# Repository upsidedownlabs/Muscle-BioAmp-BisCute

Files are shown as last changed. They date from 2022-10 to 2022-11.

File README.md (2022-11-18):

# Muscle BioAmp BisCute

 



 
 


Muscle BioAmp BisCute is a cute DIY EMG sensor for precise ElectroMyoGraphy (EMG) at an affordable cost. It comes with a fixed gain of x2420 and BandPass filter of 72Hz - 720Hz. To record the EMG signals you can use any standalone ADC like ADS1115 or any microcontroller development board with an ADC of your choice like Arduino UNO/Nano.

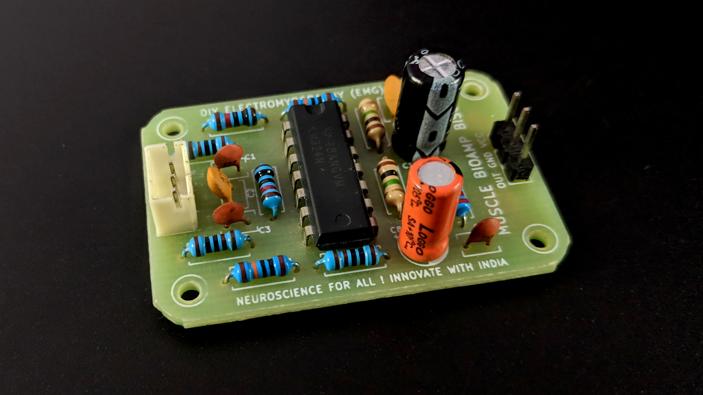
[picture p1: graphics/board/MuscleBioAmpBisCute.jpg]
Upside Down Labs BioAmp EXG Pill Assembled


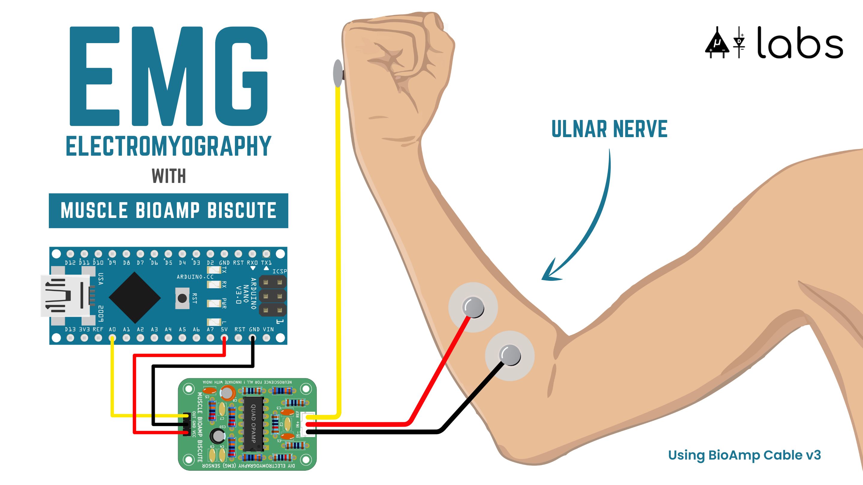
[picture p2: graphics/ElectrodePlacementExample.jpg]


## Hardware

Muscle BioAmp Biscute has been created using KiCad and all the design files can be found under [hardware](hardware/) folder. Images below shows a quick overview of the hardware design.

| PCB Front           |  PCB Back |
| :-------------------------: | :-------------------------: |
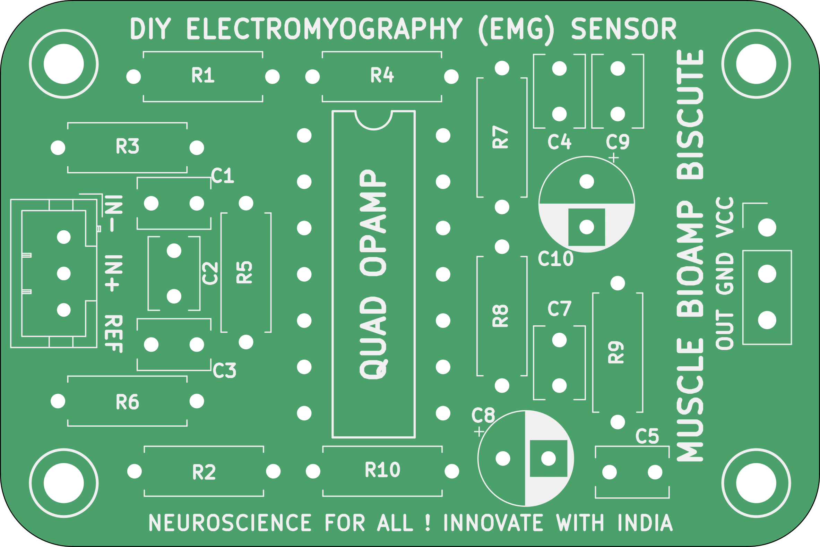
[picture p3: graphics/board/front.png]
Upside Down Labs Muscle BioAmp BisCute front
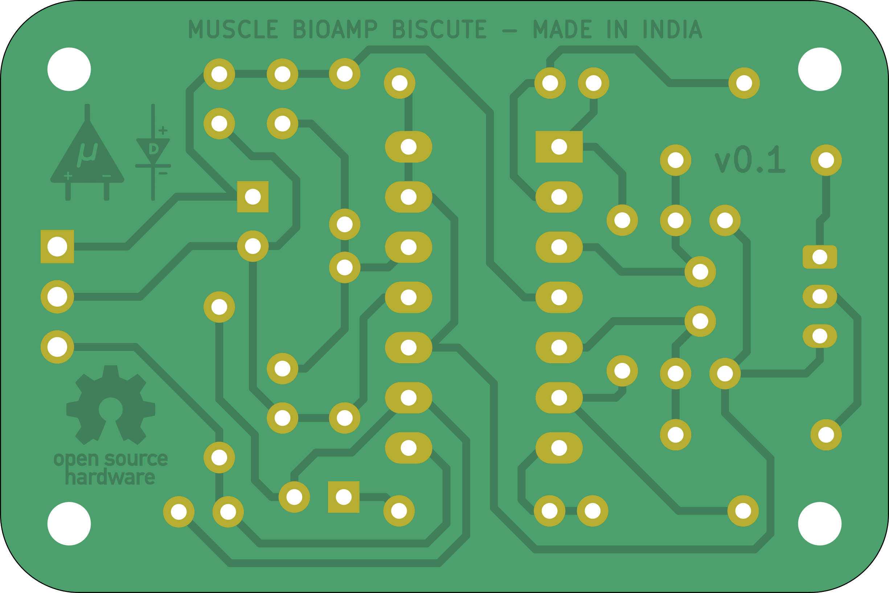
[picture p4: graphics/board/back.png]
Upside Down Labs Muscle BioAmp BisCute back
|   |  |

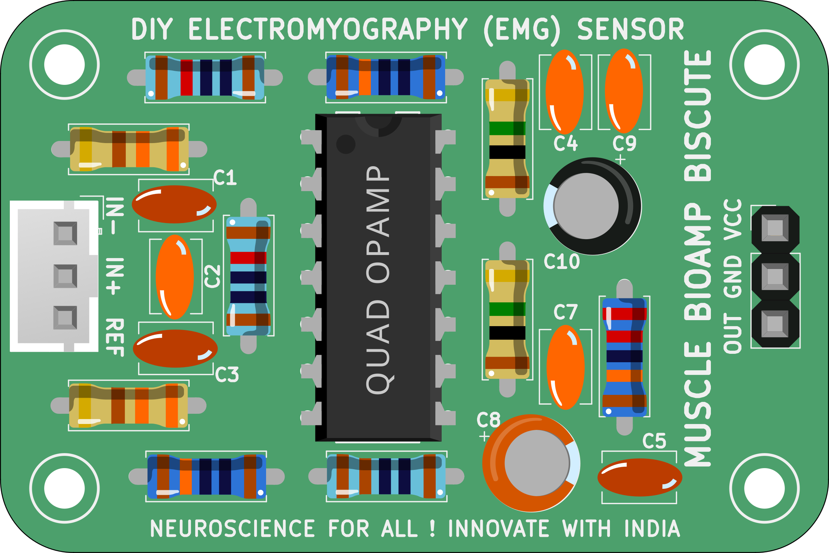
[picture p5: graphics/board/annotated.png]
Upside Down Labs Muscle BioAmp BisCute front annotated


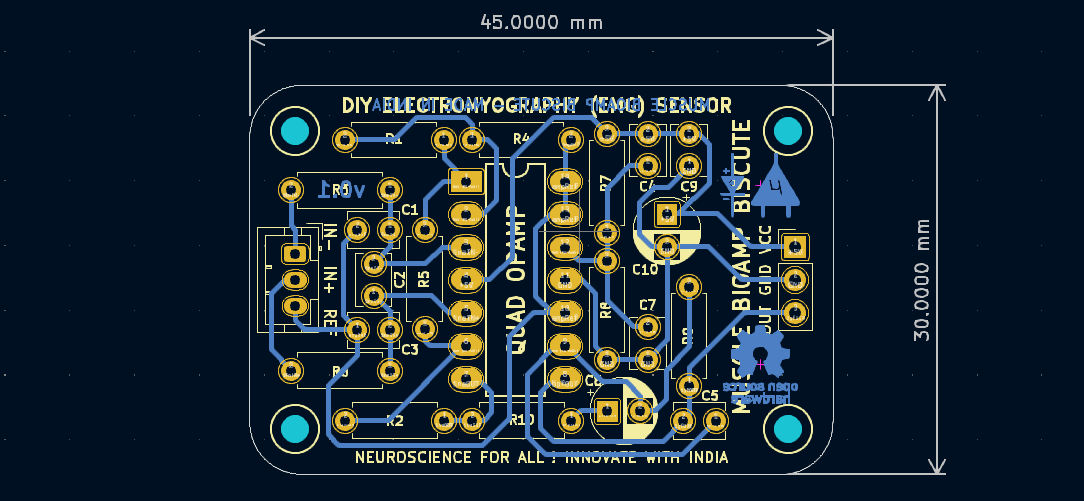
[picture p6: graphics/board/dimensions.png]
Upside Down Labs Muscle BioAmp BisCute dimensions


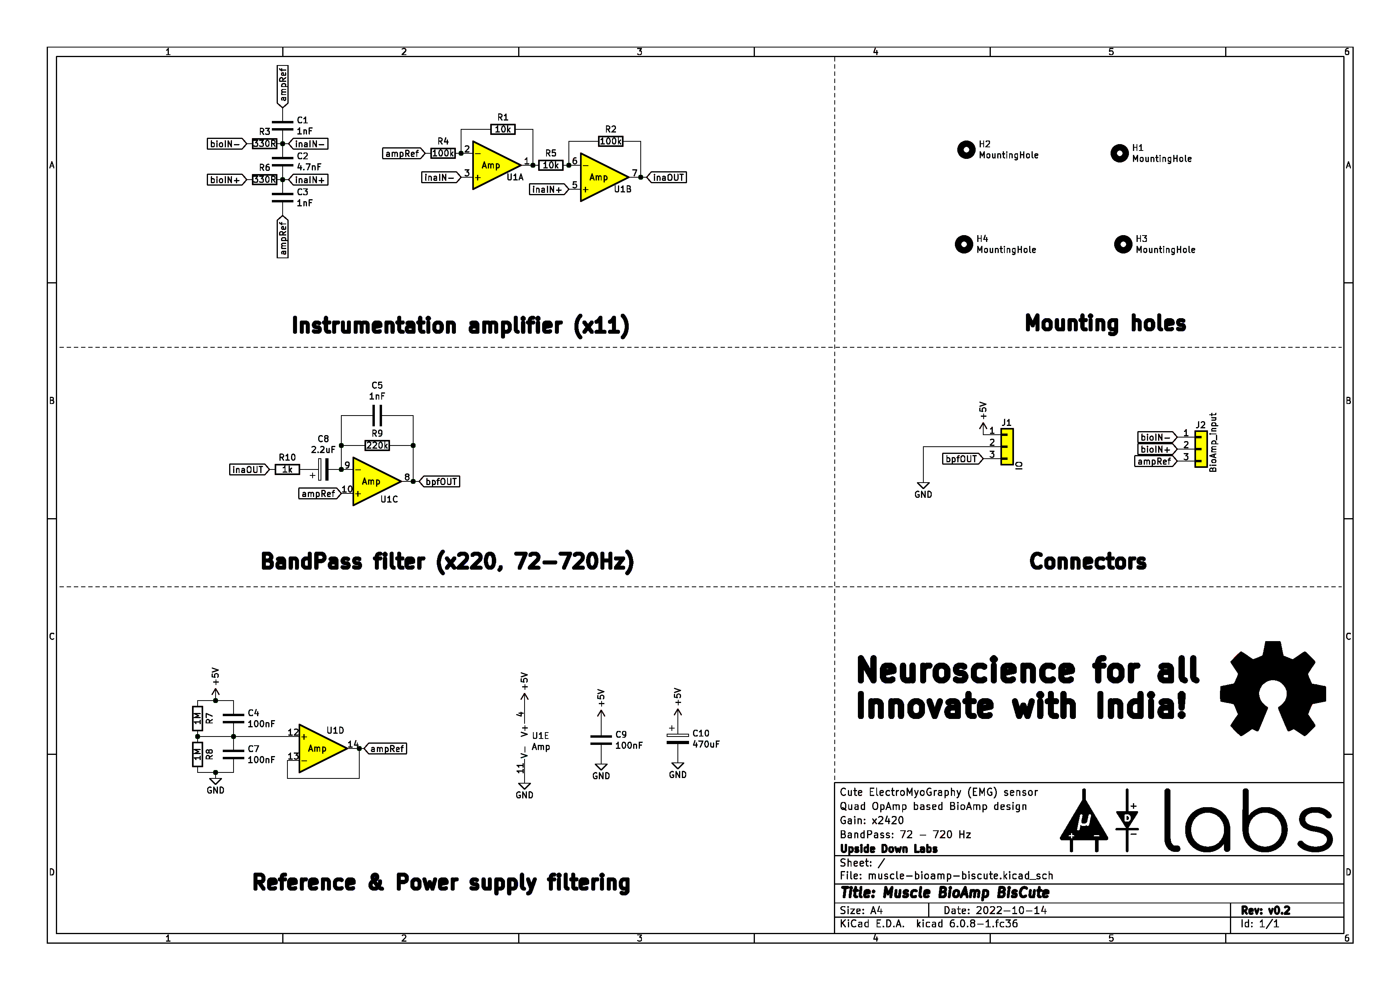
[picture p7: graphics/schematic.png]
Upside Down Labs Muscle BioAmp BisCute schematic


### Assembly

You can get your own Muscle BioAmp BisCute bag of parts from [our store](https://store.upsidedownlabs.tech/product/muscle-bioamp-biscute-diy/) or [Tindie](https://www.tindie.com/products/upsidedownlabs/muscle-bioamp-biscute-diy-muscle-sensor/) and for assembling your Biscute you can take a look at [this interactive BOM](https://upsidedownlabs.github.io/Muscle-BioAmp-BisCute/) or the step by step guide below. 

| Step 1 - Bare board | Step 2 - 100K Resistor | Step 3 - 10K Resistor| Step 4 - 1M Resistor|
| :----: | :----: | :----: | :----: |
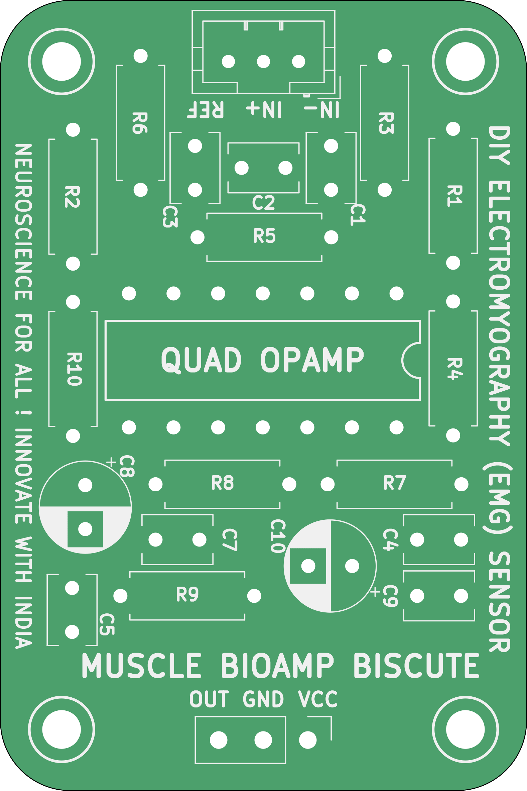
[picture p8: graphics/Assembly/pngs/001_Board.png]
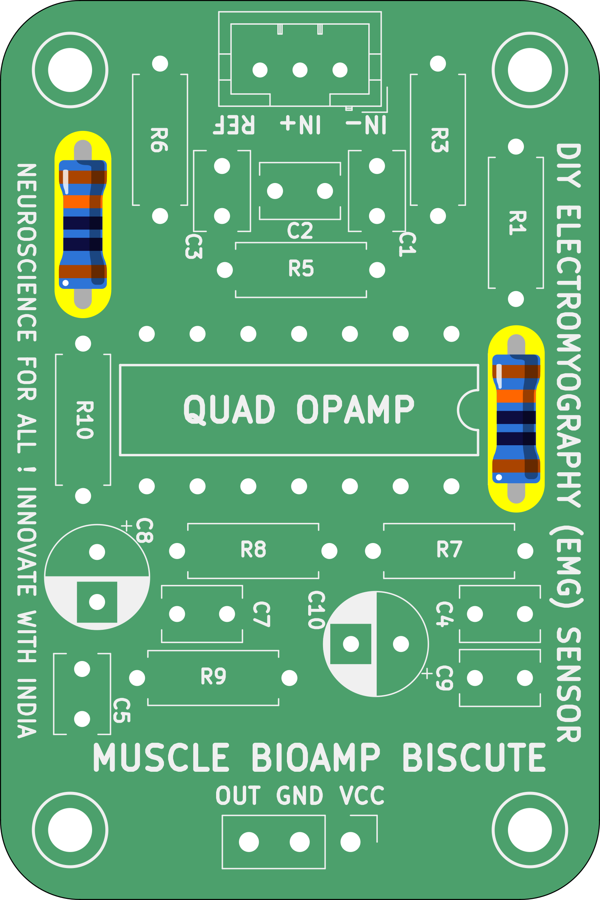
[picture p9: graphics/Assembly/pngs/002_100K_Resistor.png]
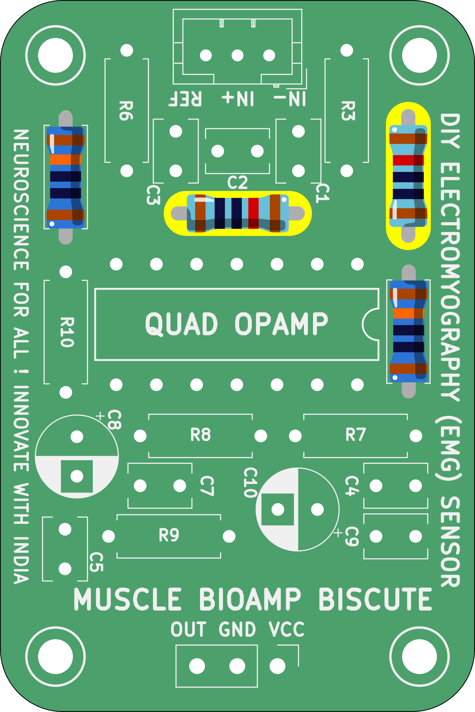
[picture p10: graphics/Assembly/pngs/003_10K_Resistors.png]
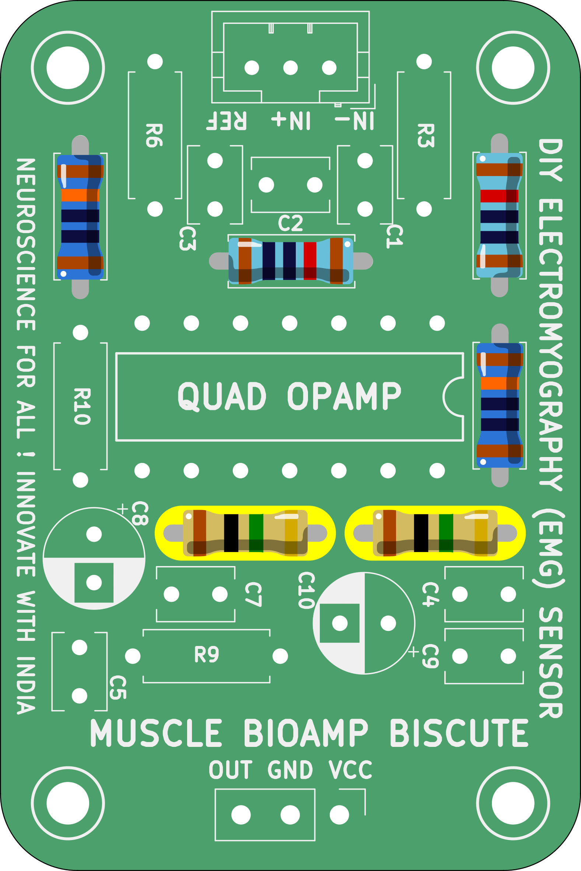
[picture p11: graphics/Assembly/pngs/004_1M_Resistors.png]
| ||||

| Step 5 - 330R Resistor | Step 6 - 220K Resistor | Step 7 - 4.7nF Capacitor | Step 8 - 2.2uF Capacitor |
| :----: | :----: | :----: | :----: |
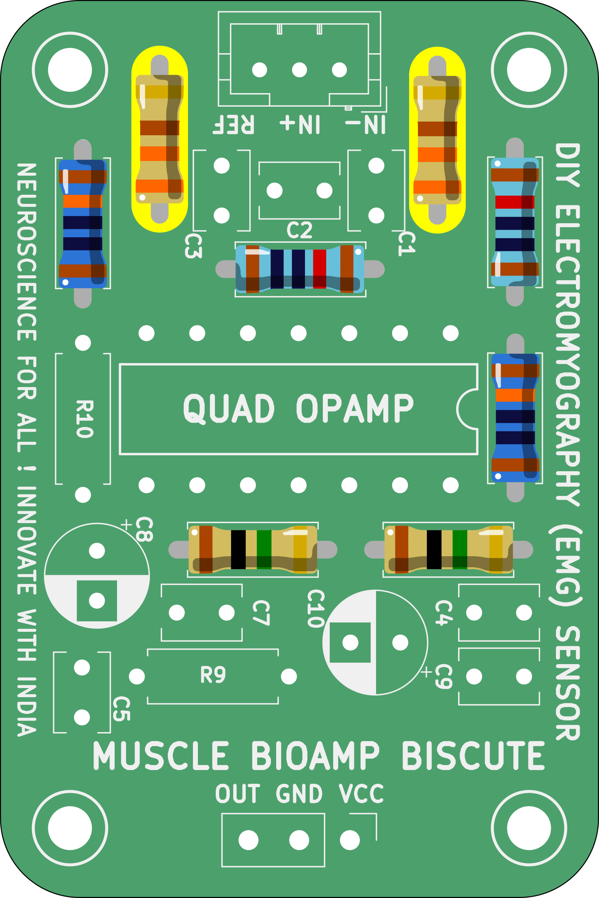
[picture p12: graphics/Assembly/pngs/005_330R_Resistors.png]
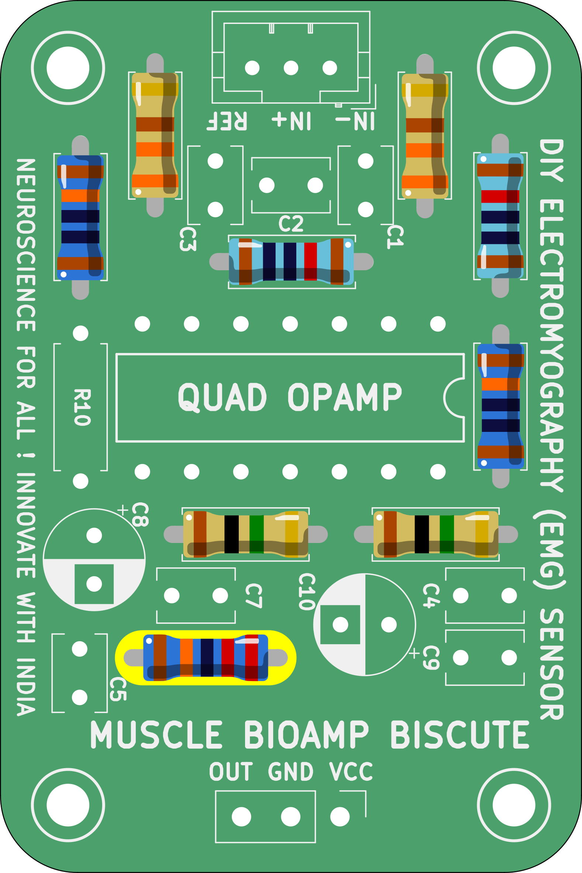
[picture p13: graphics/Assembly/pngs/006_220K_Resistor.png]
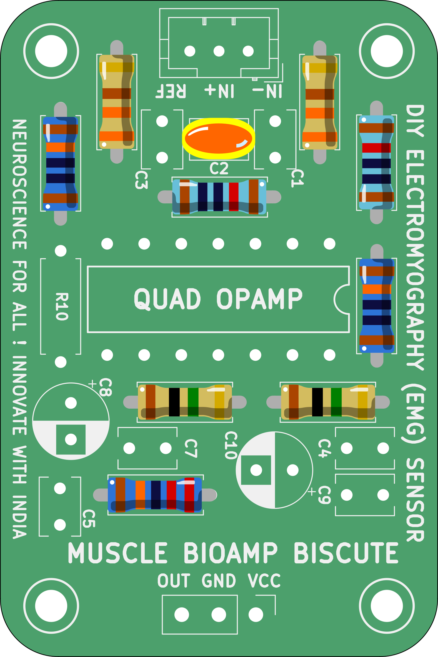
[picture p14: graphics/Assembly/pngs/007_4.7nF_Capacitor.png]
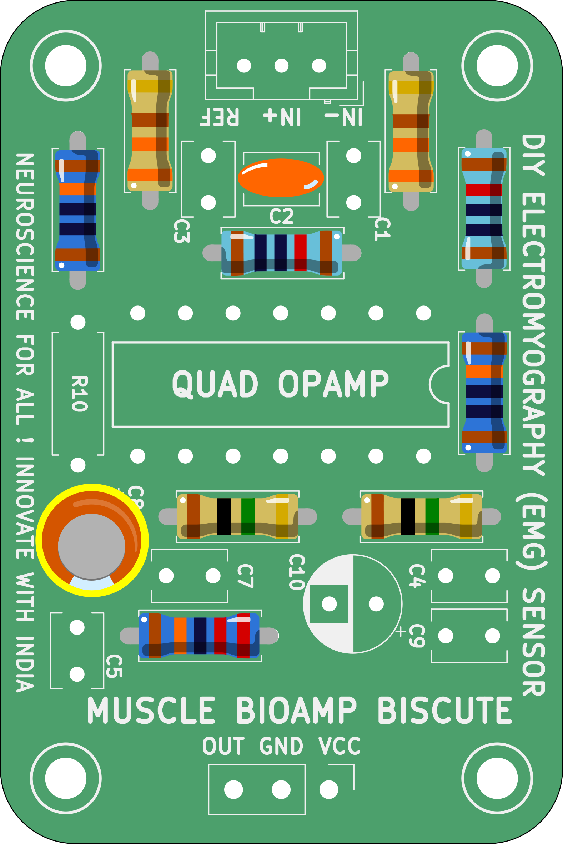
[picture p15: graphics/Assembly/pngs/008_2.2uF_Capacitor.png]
| ||||

| Step 9 - 470uF Capacitor | Step 10 - 100nF Capacitor | Step 11 - 1nF Capacitor | Step 13 - 1K Resistor |
| :----: | :----: | :----: | :----: |
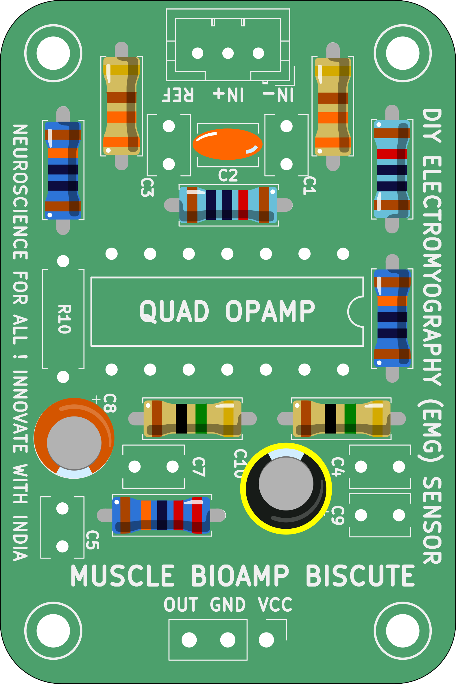
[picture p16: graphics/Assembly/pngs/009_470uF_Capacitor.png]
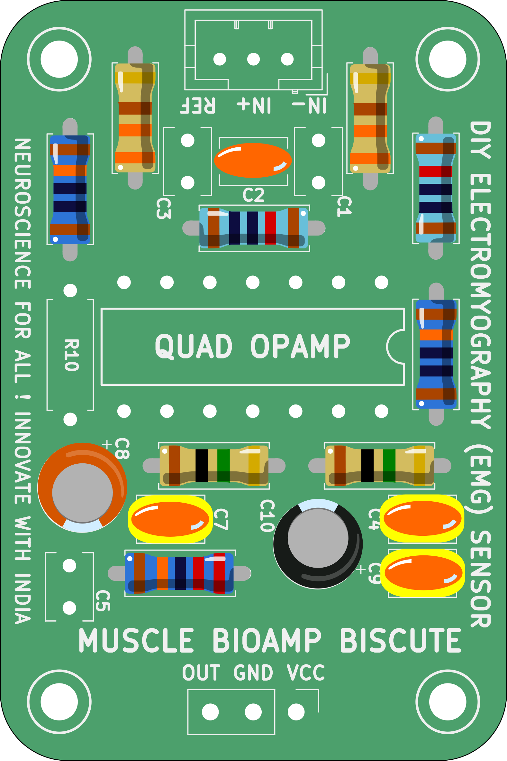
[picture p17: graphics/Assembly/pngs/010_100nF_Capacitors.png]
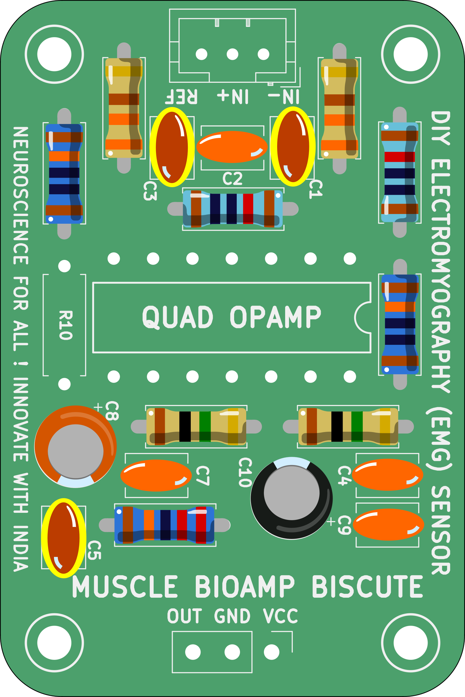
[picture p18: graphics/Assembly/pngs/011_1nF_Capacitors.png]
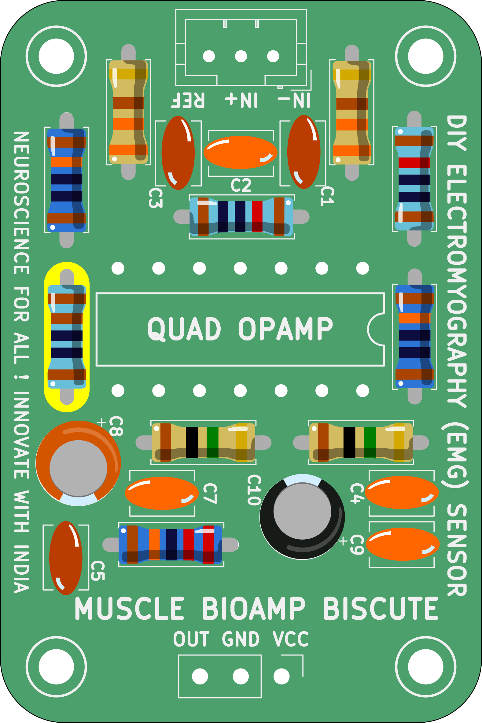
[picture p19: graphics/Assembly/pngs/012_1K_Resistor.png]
| ||||

| Step 13 - BioAmp Connector | Step 14 - Header Pin | Step 15 - IC | Step 16 - Biscute ready |
| :----: | :----: | :----: | :----: |
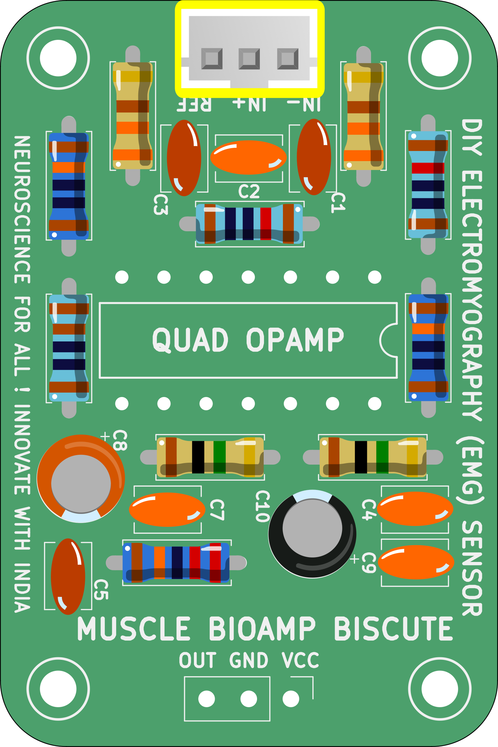
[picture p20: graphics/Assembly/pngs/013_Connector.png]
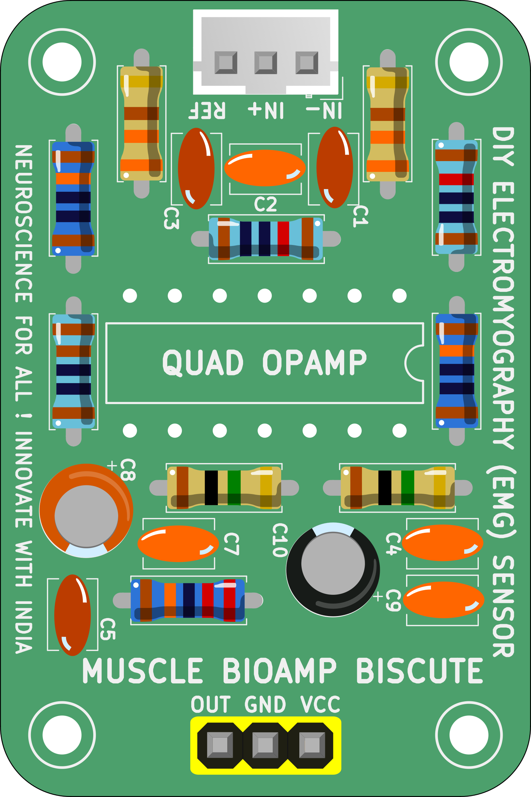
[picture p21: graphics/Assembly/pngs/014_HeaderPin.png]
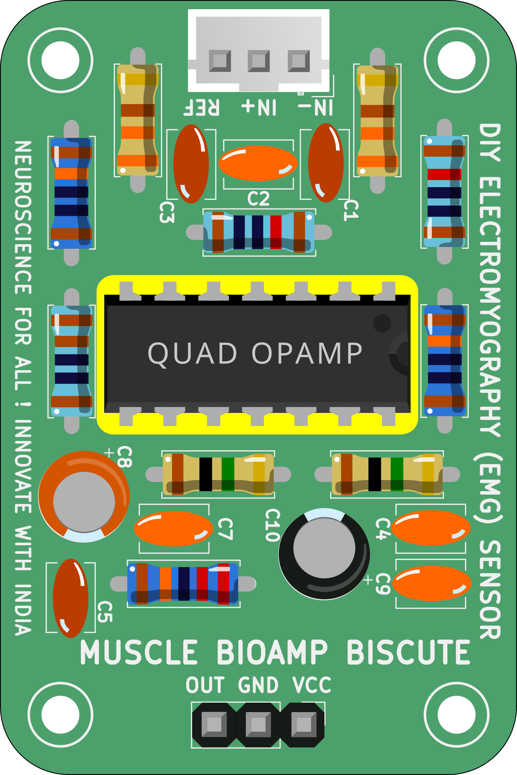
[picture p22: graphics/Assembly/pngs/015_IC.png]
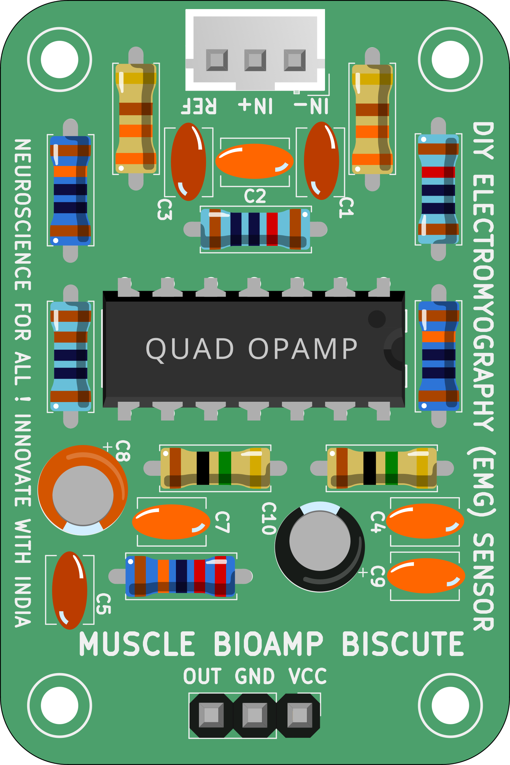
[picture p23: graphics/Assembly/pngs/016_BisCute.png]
| ||||

## License

| Licenses Facts              |  OSHWA Certification |
| :-------------------------: | :-------------------------: |
| <a href="LICENSE.md">Open Source Licenses Facts</a>  | <a href="https://certification.oshwa.org/in000039.html">Open Source Hardware Certification mark</a> | 

#### Hardware
CERN Open Hardware License Version 2 - Strongly Reciprocal ([CERN-OHL-S-2.0](https://spdx.org/licenses/CERN-OHL-S-2.0.html)).

#### Software
MIT open source [license](http://opensource.org/licenses/MIT).

#### Documentation:
<br />This work is licensed under a <a rel="license" href="http://creativecommons.org/licenses/by/4.0/">Creative Commons Attribution 4.0 International License</a>.

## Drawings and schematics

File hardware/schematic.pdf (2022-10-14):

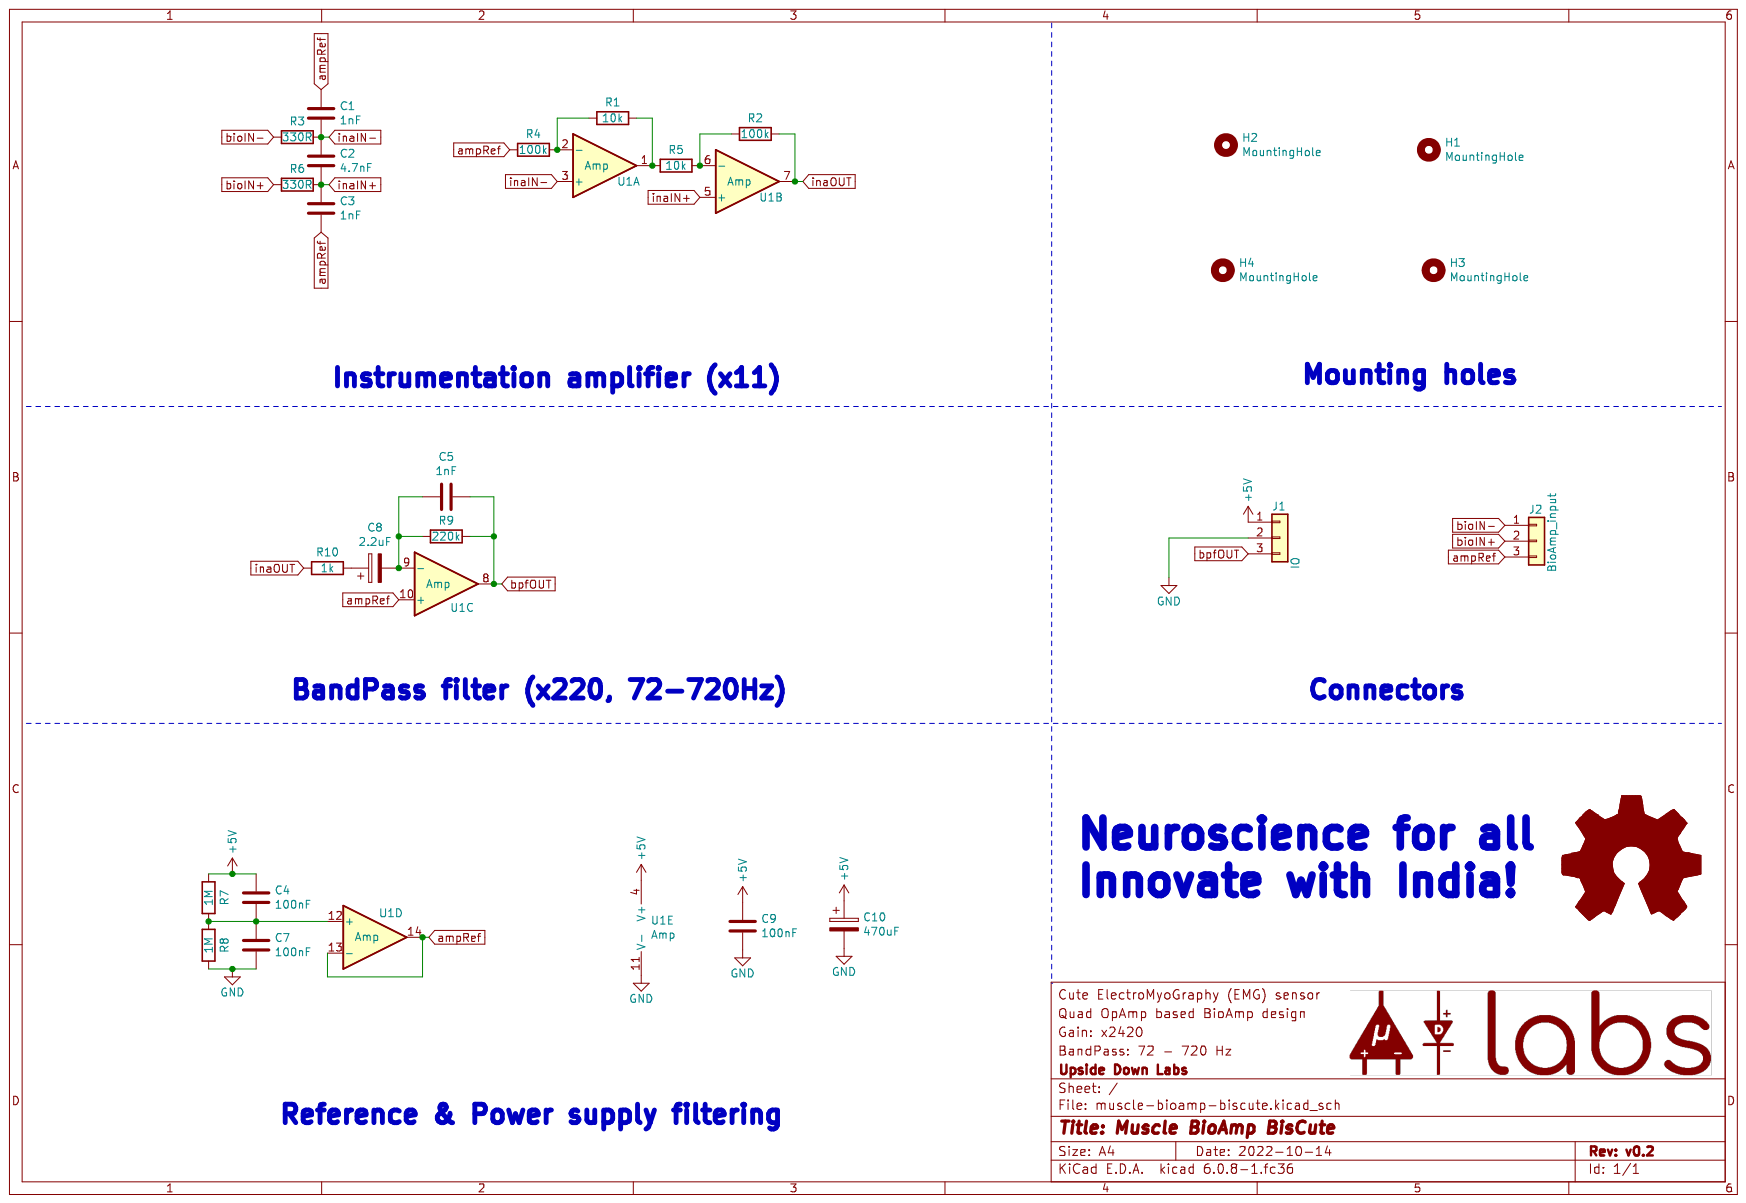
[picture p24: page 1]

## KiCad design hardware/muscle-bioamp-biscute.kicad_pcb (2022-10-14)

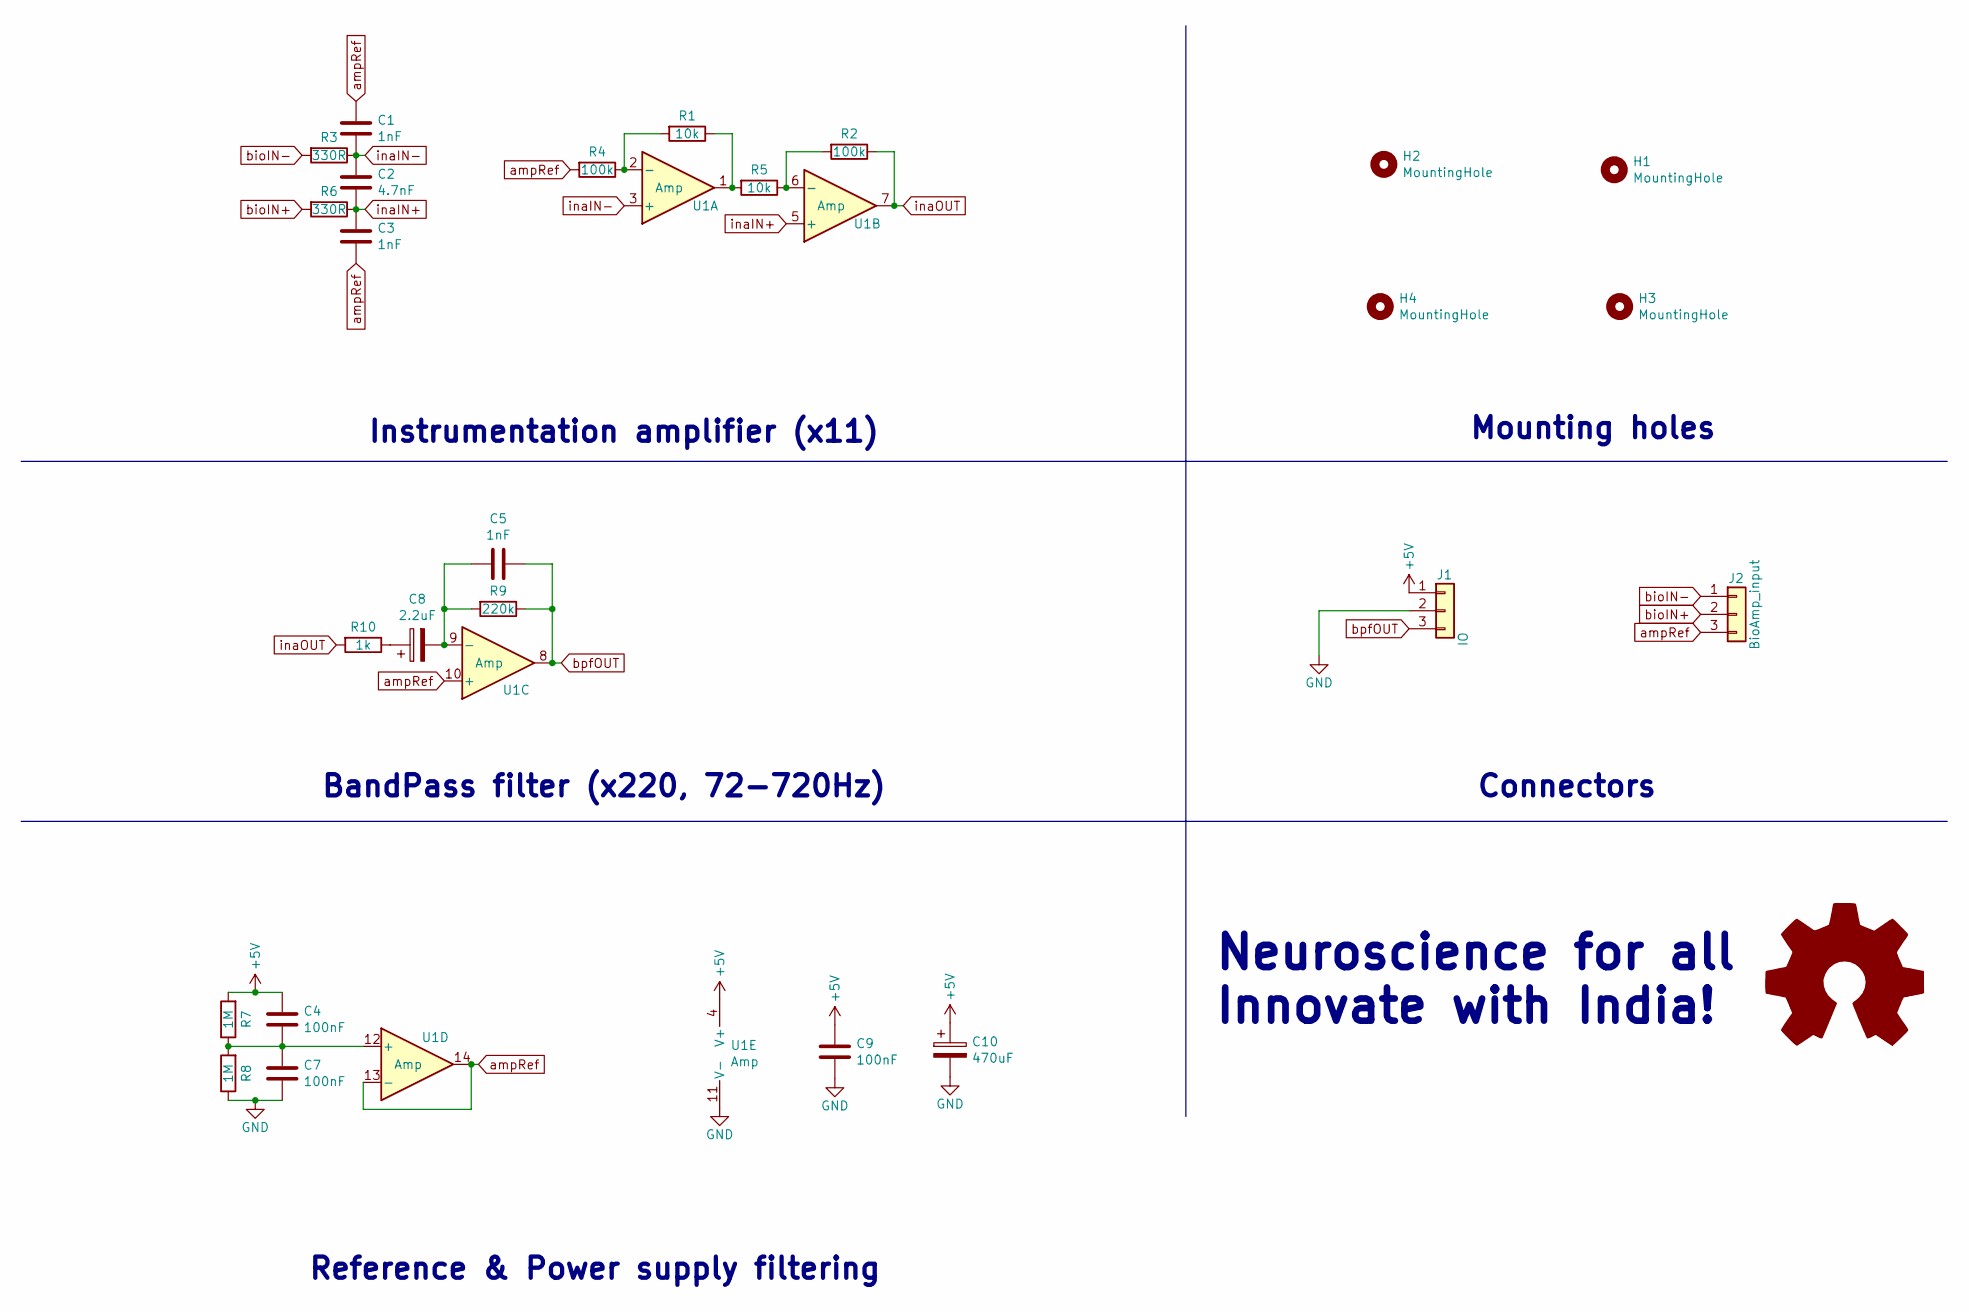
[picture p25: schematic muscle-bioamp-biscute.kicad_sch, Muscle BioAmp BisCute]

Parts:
C1, C3, C5: 1nF; C_Disc_D3.8mm_W2.6mm_P2.50mm
C2: 4.7nF; C_Disc_D3.8mm_W2.6mm_P2.50mm
C4, C7, C9: 100nF; C_Disc_D3.8mm_W2.6mm_P2.50mm
C8: 2.2uF; CP_Radial_D5.0mm_P2.50mm
C10: 470uF; CP_Radial_D5.0mm_P2.50mm
H1, H2, H3, H4: MountingHole; MountingHole_2.2mm_M2
J1: IO; PinHeader_1x03_P2.54mm_Vertical
J2: BioAmp_input; JST_PH_B3B-PH-K_1x03_P2.00mm_Vertical
R1, R5: 10k; R_Axial_DIN0207_L6.3mm_D2.5mm_P7.62mm_Horizontal
R2, R4: 100k; R_Axial_DIN0207_L6.3mm_D2.5mm_P7.62mm_Horizontal
R3, R6: 330R; R_Axial_DIN0207_L6.3mm_D2.5mm_P7.62mm_Horizontal
R7, R8: 1M; R_Axial_DIN0207_L6.3mm_D2.5mm_P7.62mm_Horizontal
R9: 220k; R_Axial_DIN0207_L6.3mm_D2.5mm_P7.62mm_Horizontal
R10: 1k; R_Axial_DIN0207_L6.3mm_D2.5mm_P7.62mm_Horizontal
U1: Amp; DIP-14_W7.62mm_LongPads

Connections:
+5V: C4.2, C9.2, C10.1, J1.1, R7.2, U1.4 (V+)
GND: C7.1, C9.1, C10.2, J1.2, R8.1, U1.11 (V-)
unnamed: C4.1, C7.2, R7.1, R8.2, U1.12 (+)
unnamed: C5.1, C8.2, R9.2, U1.9 (-)
unnamed: C8.1, R10.1
unnamed: R1.1, R5.2, U1.1
unnamed: R1.2, R4.1, U1.2 (-)
unnamed: R2.2, R5.1, U1.6 (-)
ampRef: C1.2, C3.1, J2.3, R4.2, U1.10 (+), U1.13 (-), U1.14
bioIN+: J2.2, R6.2
bioIN-: J2.1, R3.2
bpfOUT: C5.2, J1.3, R9.1, U1.8
inaIN+: C2.1, C3.2, R6.1, U1.5 (+)
inaIN-: C1.1, C2.2, R3.1, U1.3 (+)
inaOUT: R2.1, R10.2, U1.7

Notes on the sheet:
Instrumentation amplifier (x11)
Reference & Power supply filtering
Neuroscience for all Innovate with India!
Connectors
BandPass filter (x220, 72-720Hz)
Mounting holes

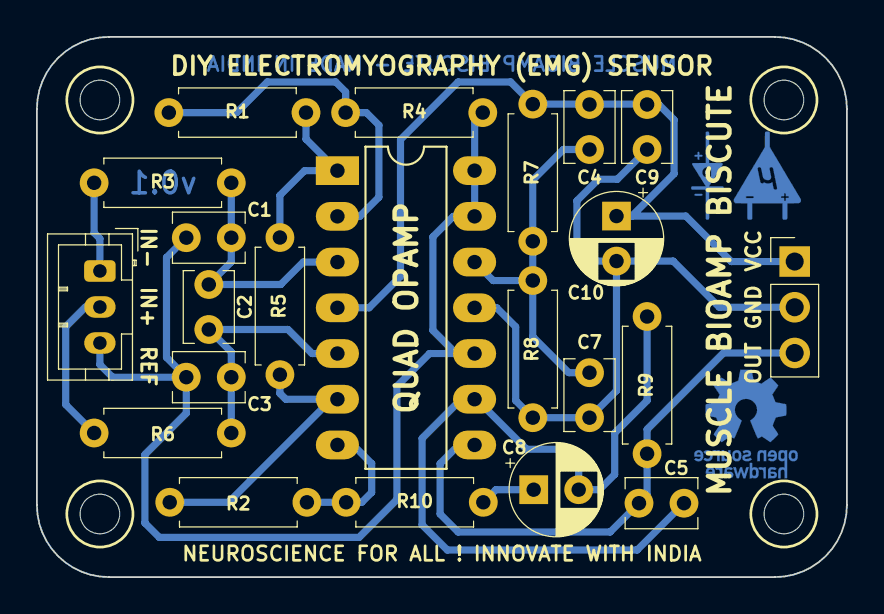
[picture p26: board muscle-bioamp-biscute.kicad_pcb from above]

Board: 2 copper layers, 45.0 x 30.0 mm, 26 parts (0 on the bottom side), 15 nets.

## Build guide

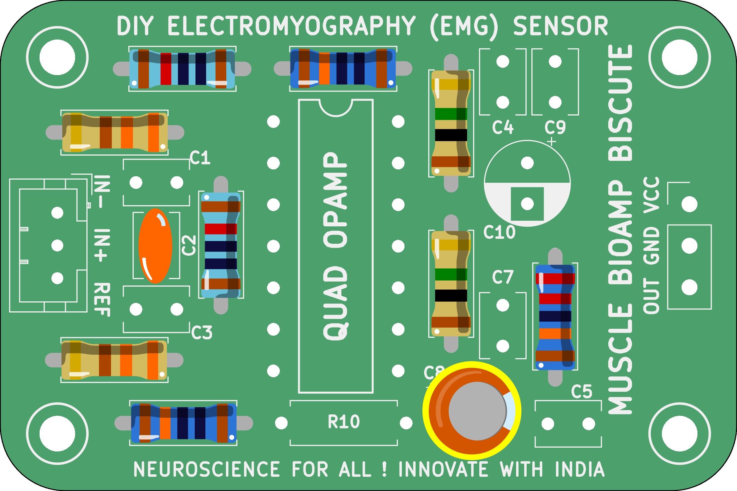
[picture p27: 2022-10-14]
graphics/Assembly/008_2.2uF_Capacitor.jpg

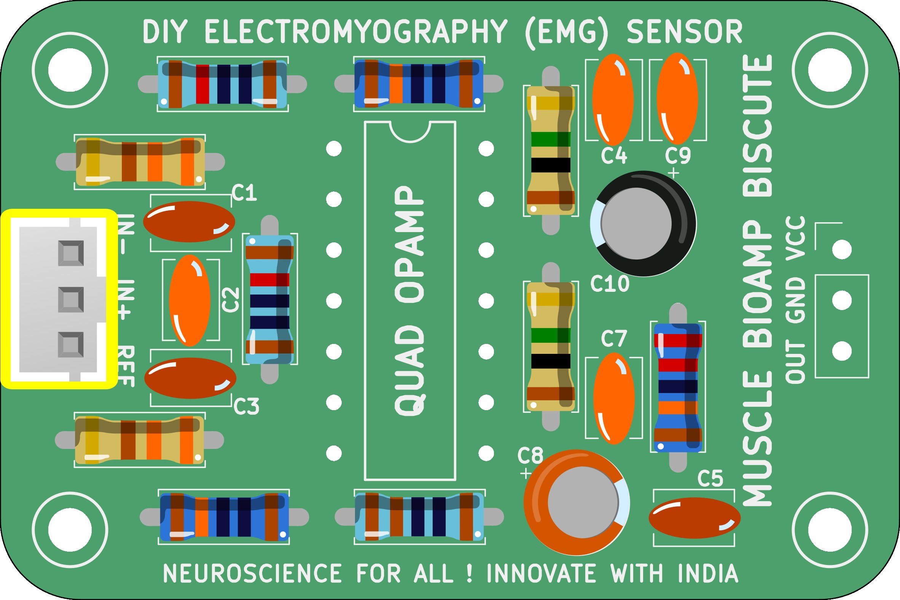
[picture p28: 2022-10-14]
graphics/Assembly/013_Connector.jpg

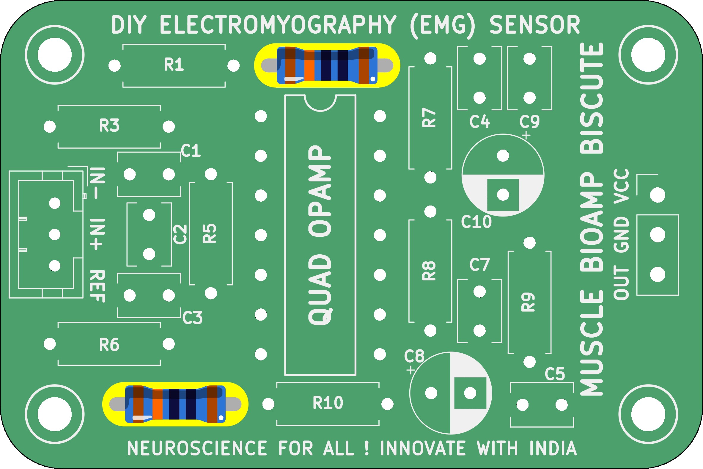
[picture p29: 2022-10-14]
graphics/Assembly/002_100K_Resistor.jpg

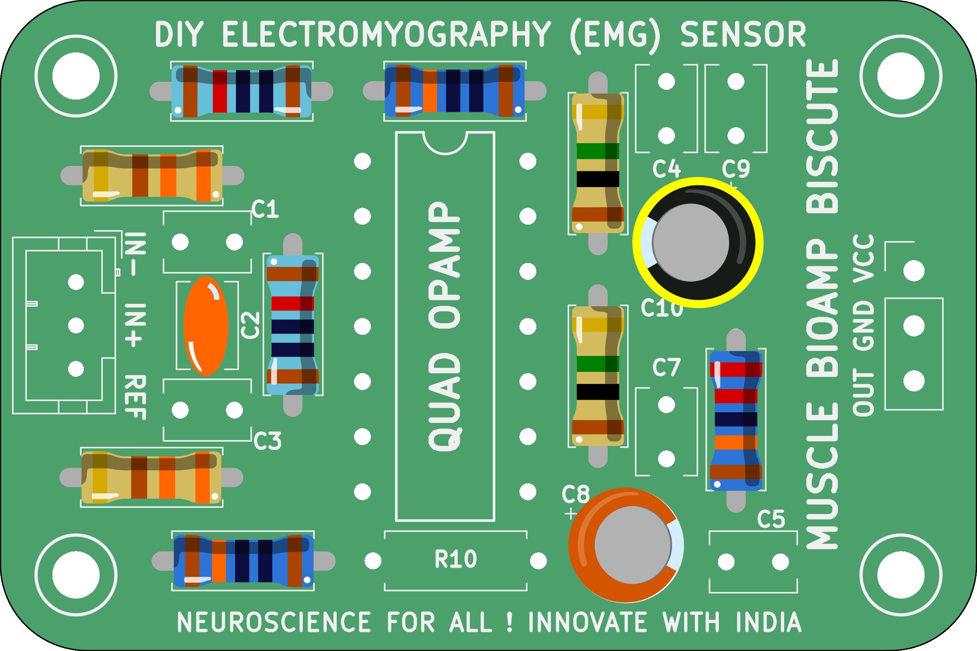
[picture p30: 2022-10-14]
graphics/Assembly/009_470uF_Capacitor.jpg

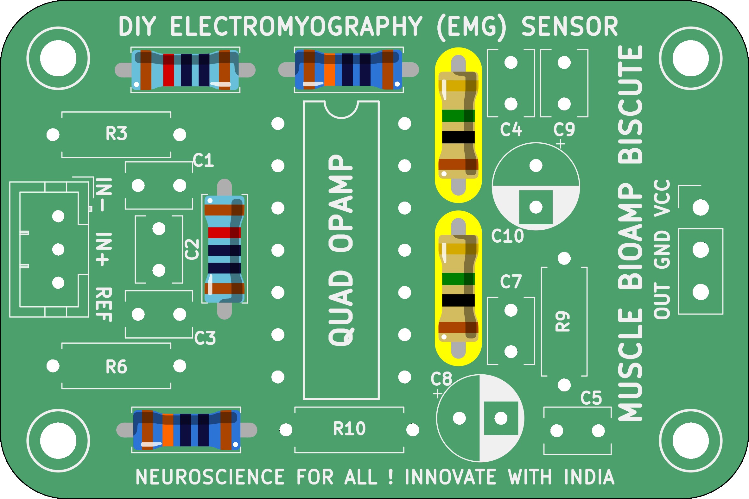
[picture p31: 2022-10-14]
graphics/Assembly/004_1M_Resistors.jpg

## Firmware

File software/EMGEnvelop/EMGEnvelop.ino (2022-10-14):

// EMG Envelop - Muscle BioAmp BisCute
// https://github.com/upsidedownlabs/Muscle-BioAmp-BisCute

// Upside Down Labs invests time and resources providing this open source code,
// please support Upside Down Labs and open-source hardware by purchasing
// products from Upside Down Labs!

// Copyright (c) 2021-2022 Upside Down Labs - contact@upsidedownlabs.tech

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
#define SAMPLE_RATE 500
#define BAUD_RATE 115200
#define INPUT_PIN A0
#define BUFFER_SIZE 128

int circular_buffer[BUFFER_SIZE];
int data_index, sum;

void setup() {
	// Serial connection begin
	Serial.begin(BAUD_RATE);
}

void loop() {
	// Calculate elapsed time
	static unsigned long past = 0;
	unsigned long present = micros();
	unsigned long interval = present - past;
	past = present;

	// Run timer
	static long timer = 0;
	timer -= interval;

	// Sample and get envelop
	if(timer < 0) {
		timer += 1000000 / SAMPLE_RATE;
		int sensor_value = analogRead(INPUT_PIN);
		int signal = EMGFilter(sensor_value);
		int envelop = getEnvelop(abs(signal));
		Serial.print(signal);
		Serial.print(",");
		Serial.println(envelop);
	}
}

// Envelop detection algorithm
int getEnvelop(int abs_emg){
	sum -= circular_buffer[data_index];
	sum += abs_emg;
	circular_buffer[data_index] = abs_emg;
	data_index = (data_index + 1) % BUFFER_SIZE;
	return (sum/BUFFER_SIZE) * 2;
}

// Band-Pass Butterworth IIR digital filter, generated using filter_gen.py.
// Sampling rate: 500.0 Hz, frequency: [74.5, 149.5] Hz.
// Filter is order 4, implemented as second-order sections (biquads).
// Reference: 
// https://docs.scipy.org/doc/scipy/reference/generated/scipy.signal.butter.html
// https://courses.ideate.cmu.edu/16-223/f2020/Arduino/FilterDemos/filter_gen.py
float EMGFilter(float input)
{
  float output = input;
  {
    static float z1, z2; // filter section state
    float x = output - 0.05159732*z1 - 0.36347401*z2;
    output = 0.01856301*x + 0.03712602*z1 + 0.01856301*z2;
    z2 = z1;
    z1 = x;
  }
  {
    static float z1, z2; // filter section state
    float x = output - -0.53945795*z1 - 0.39764934*z2;
    output = 1.00000000*x + -2.00000000*z1 + 1.00000000*z2;
    z2 = z1;
    z1 = x;
  }
  {
    static float z1, z2; // filter section state
    float x = output - 0.47319594*z1 - 0.70744137*z2;
    output = 1.00000000*x + 2.00000000*z1 + 1.00000000*z2;
    z2 = z1;
    z1 = x;
  }
  {
    static float z1, z2; // filter section state
    float x = output - -1.00211112*z1 - 0.74520226*z2;
    output = 1.00000000*x + -2.00000000*z1 + 1.00000000*z2;
    z2 = z1;
    z1 = x;
  }
  return output;
}

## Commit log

2022-10-14 Muscle BioAmp BisCute KiCad files
    [muscle-bioamp-biscute.kicad_pcb, muscle-bioamp-biscute.kicad_sch]
2022-10-14 Add bom/assembly html
2022-10-14 Add board and assembly graphics
2022-10-14 Update board graphics
2022-11-10 Update readme & assembly diagrams
